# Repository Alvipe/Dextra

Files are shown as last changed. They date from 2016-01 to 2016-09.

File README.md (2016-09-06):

# Dextra
Dextra is a printable robotic hand with the size of a human hand. This project was initially started to build a replicable and low cost alternative to current robotic hand prostheses. However, I think this device has more potential uses, for example in robotics research (humanoid robotics, mobile platforms with manipulation capabilities) or in education, fields that could benefit from the existence of a cheap and easy to repair robotic hand, a robotic device that is replicable and hackable, and simple but functional.

<p align="center">
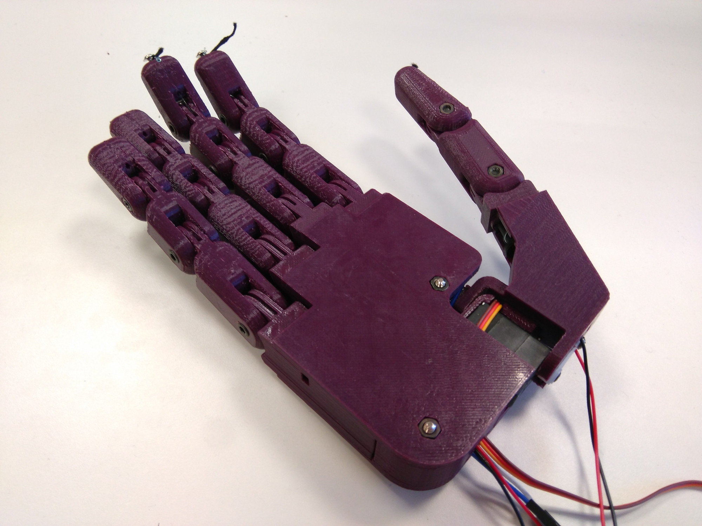
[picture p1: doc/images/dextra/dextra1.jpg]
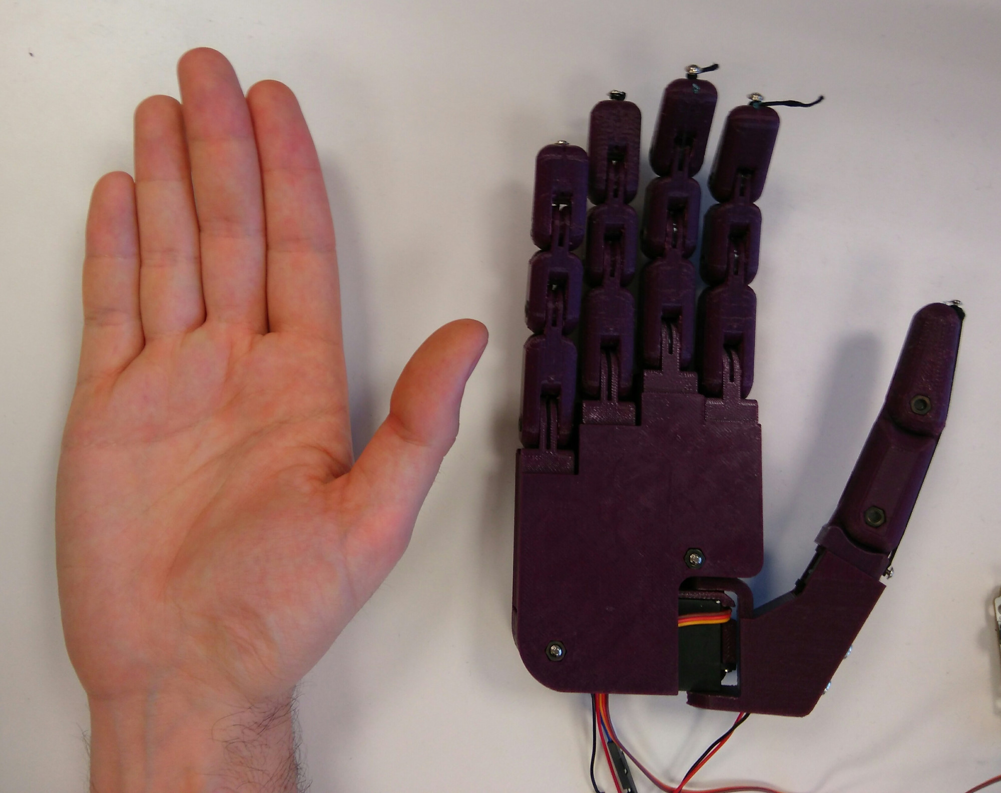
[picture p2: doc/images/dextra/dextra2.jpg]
    
</p>

The key design points of Dextra are: adaptive grip, compact size, mechanical simplicity and ease of replication. The mechanical design of Dextra revolves around the finger module the finger module, a modular part that comprises a compact linear actuator based on the Pololu 1000:1 Micro Metal Gearmotor HP, position feedback provided by a magnetic encoder, and the mechanical printable finger. This module is used in the four fingers of the hand, and the thumb is a variation of the same design. This makes assembly and repair simpler. Modular design also may favour the possibility of modifying the original design.

<p align="center">
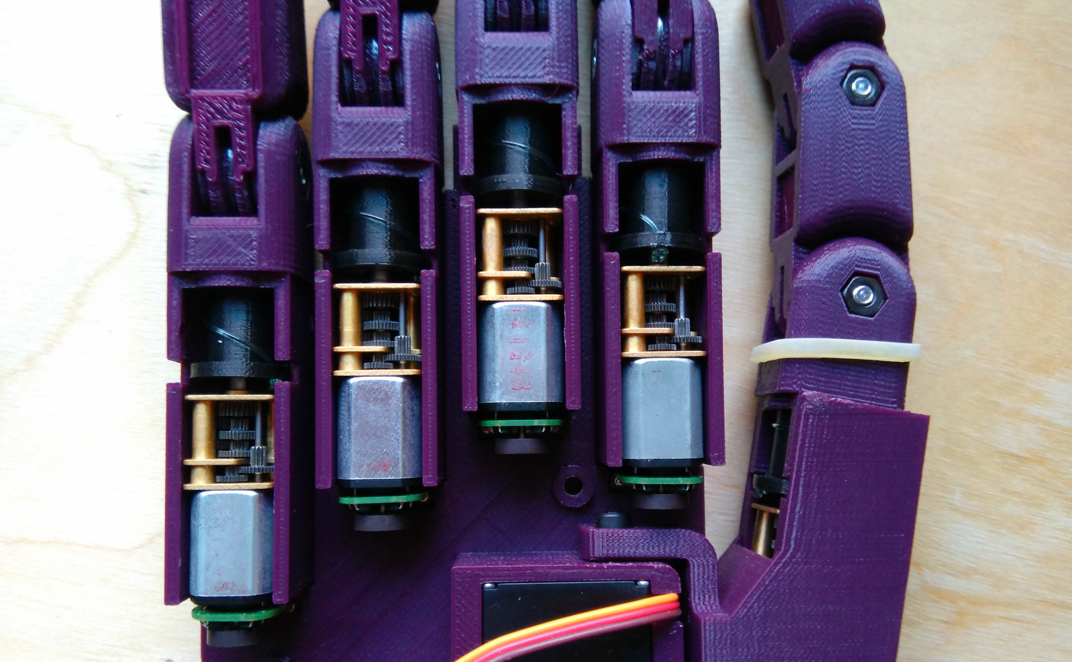
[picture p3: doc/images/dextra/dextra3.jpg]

</p>

The motion of the fingers of Dextra is controlled by a position control loop. Since the finger is underactuated, the angular position of each phalanx cannot be controlled independently. Instead, the total angular position of the finger, that is, the sum of the three joint angles, is controlled. Each finger is controlled by a PID loop that takes a position setpoint as the input and uses the feedback position measured by a magnetic quadrature encoder to adjust the real position of the DC motor driving the finger.

Dextra can be controlled either by sending commands from a computer with a GUI, or by using EMG signals, as would be done if the hand is used as a prosthesis. To implement the second type of control, an EMG interface called [Mumai](https://github.com/Alvipe/Mumai) is being used. Currently, a myoelectric threshold controller is implemented: the raw EMG signal provided by the EMG interface is rectified and smoothed by software and when this processed signal exceeds a certain value, the hand closes.

There is more information about Dextra on its [hackaday.io project page](https://hackaday.io/project/9890-dextra).

# Assembly instructions
The assembly instructions can be found [here](https://github.com/Alvipe/Dextra/tree/master/doc/dextra_assembly_instructions.pdf).

# Project index
* [Control](https://github.com/Alvipe/Dextra/tree/master/Control) - Code for different control methods (EMG, GUI)
* [Firmware](https://github.com/Alvipe/Dextra/tree/master/Firmware) - Main program and libraries that make Dextra move
* [Parts](https://github.com/Alvipe/Dextra/tree/master/Parts) - STL files of the printable parts of Dextra and its corresponding FreeCAD source files
* [doc](https://github.com/Alvipe/Dextra/tree/master/doc) - Documentation files

# License
<a rel="license1" href="https://www.gnu.org/licenses/gpl-3.0.html">GNU License</a>  

Code is licensed under the [GPL v3 License](https://www.gnu.org/licenses/gpl-3.0.html). The rest of the work is licensed under the [Creative Commons Attribution-ShareAlike 4.0 International License](http://creativecommons.org/licenses/by-sa/4.0/).

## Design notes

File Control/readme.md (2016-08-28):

The Dextra Control GUI is designed using [Kivy](https://kivy.org/#home). Besides having Python installed, this library and its dependencies are required to run the application. The application uses both the *.py* and the *.kv* files, and they need to be in the same folder.

To run the control GUI, connect the microcontroller running the Dextra firmware to a USB port of the computer, and run:

```bash
~/Dextra$ cd Control
~/Dextra/Control$ python DextraControl.py
```

First, the device to which we want to communicate (the microcontroller running the Dextra firmware) has to be selected from a dropdown list. Once the desired device is selected (in this case the one connected to COM4; in this example the app is running on a Windows PC), we click on the connect button. If there is no device connected to the PC, or no device is selected from the dropdown list, an error message is displayed.

<p align="center">
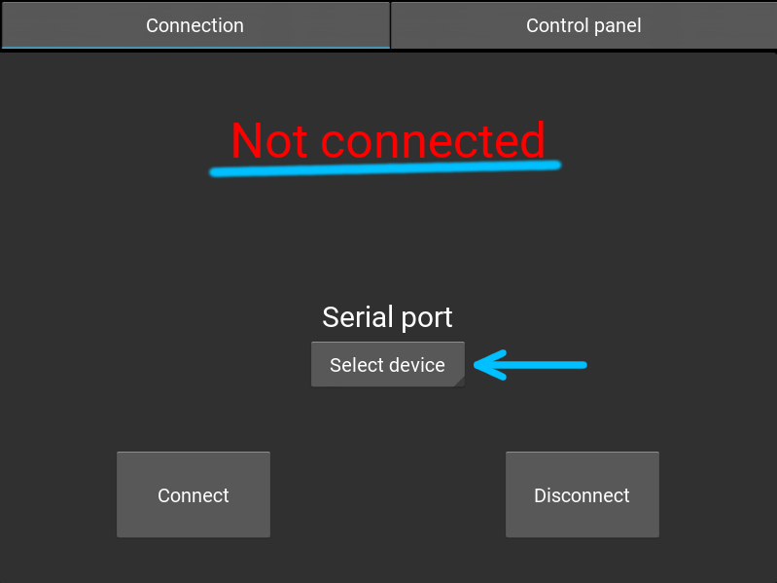
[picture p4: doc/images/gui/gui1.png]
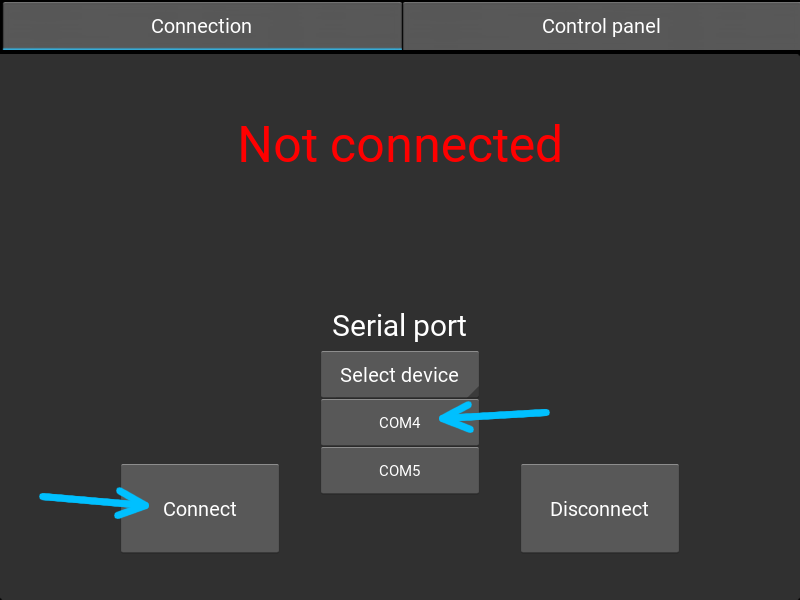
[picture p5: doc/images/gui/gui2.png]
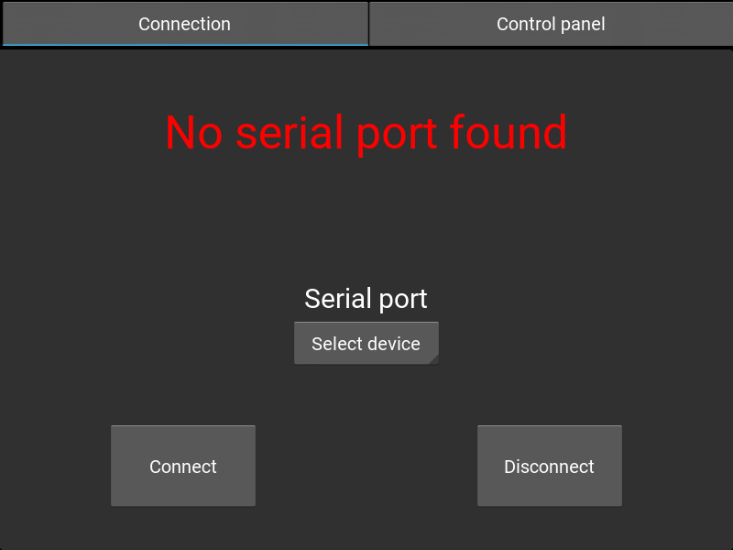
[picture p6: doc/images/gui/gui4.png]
        
</p>

If the connection is successful, we can select the *Control panel* tab. In this tab, we can control the position of each finger and the abduction angle of the thumb. The position values can be inputted by using the text boxes or by moving the sliders.

<p align="center">
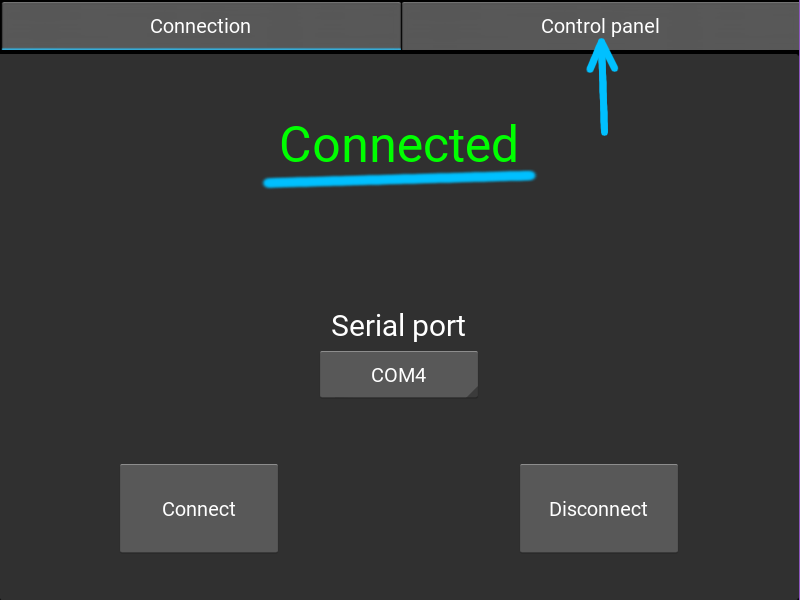
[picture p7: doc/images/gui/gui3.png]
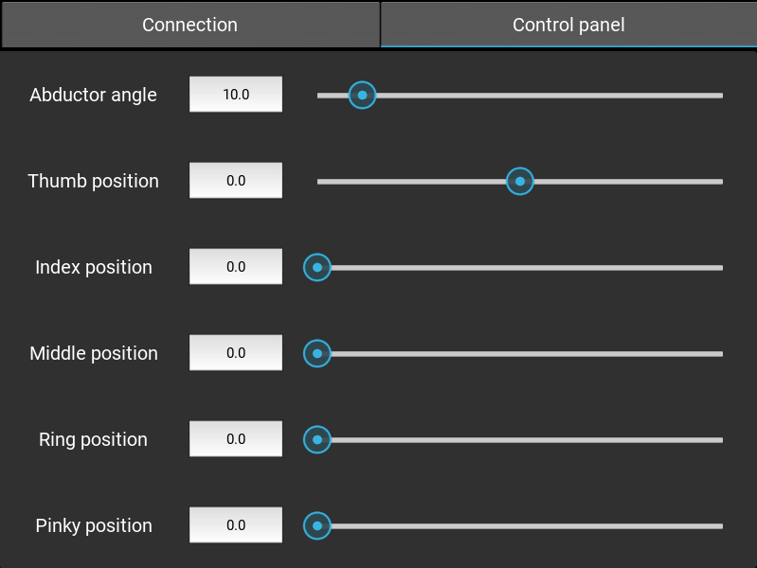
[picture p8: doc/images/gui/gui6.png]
    
</p>

To stop communicating with the microcontroller, we select the *Connection* tab and click the disconnect button.

<p align="center">
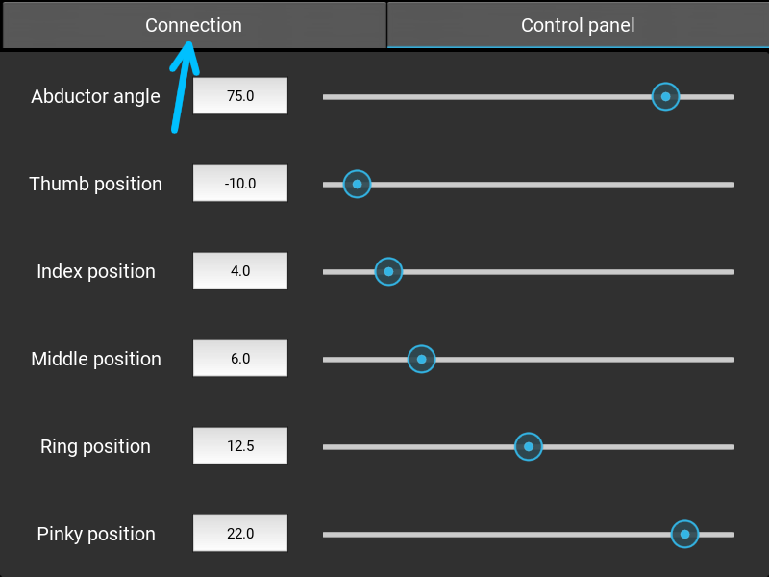
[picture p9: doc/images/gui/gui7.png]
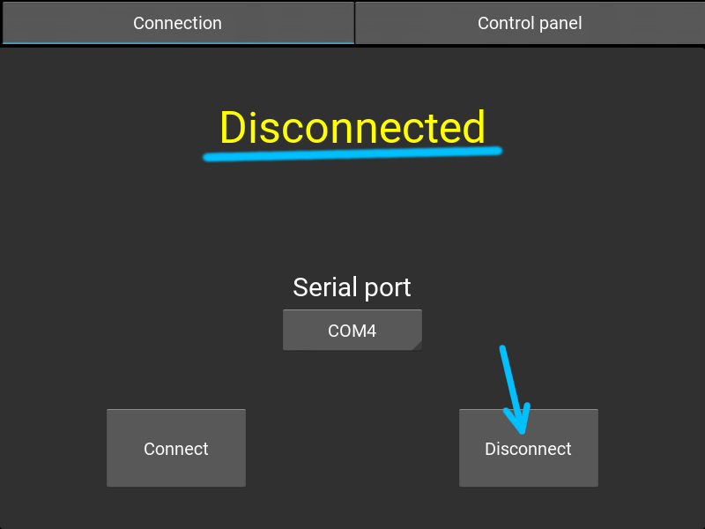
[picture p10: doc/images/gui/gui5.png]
    
</p>

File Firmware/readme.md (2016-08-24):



To upload the firmware to one of the supported boards, use [platformio](http://platformio.org/).

For Teensy 3.1 (Arduino-compatible board):
```bash
~/Dextra$ cd Firmware/Teensy31
~/Dextra/Firmware/Teensy31$ platformio run --target upload
```

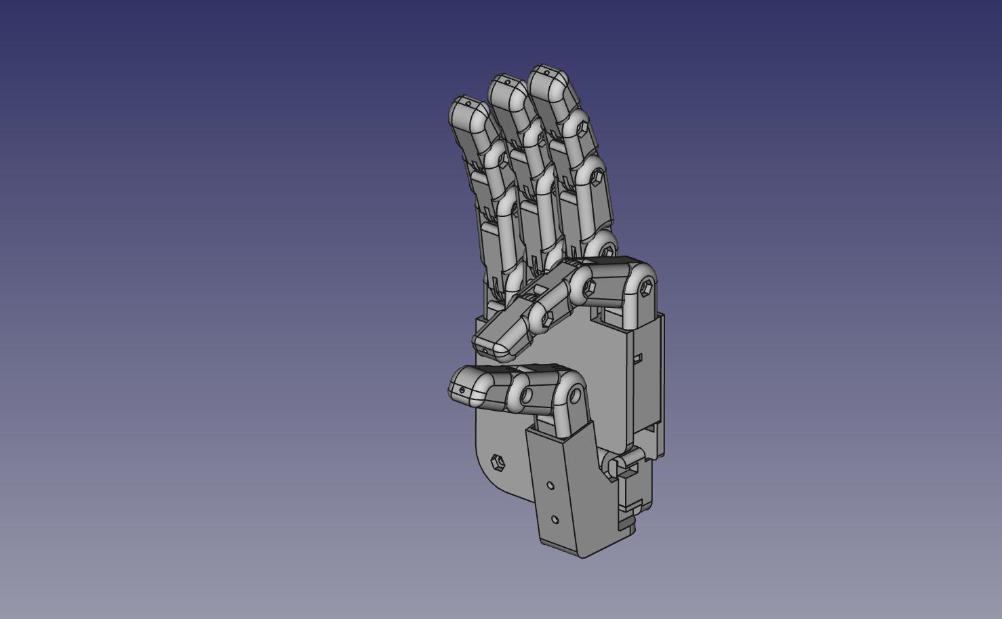
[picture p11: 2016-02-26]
doc/images/dextra/palmar_pinch_grasp.jpg

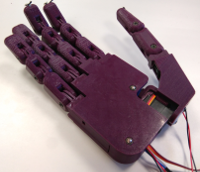
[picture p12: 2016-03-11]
doc/images/dextra.png

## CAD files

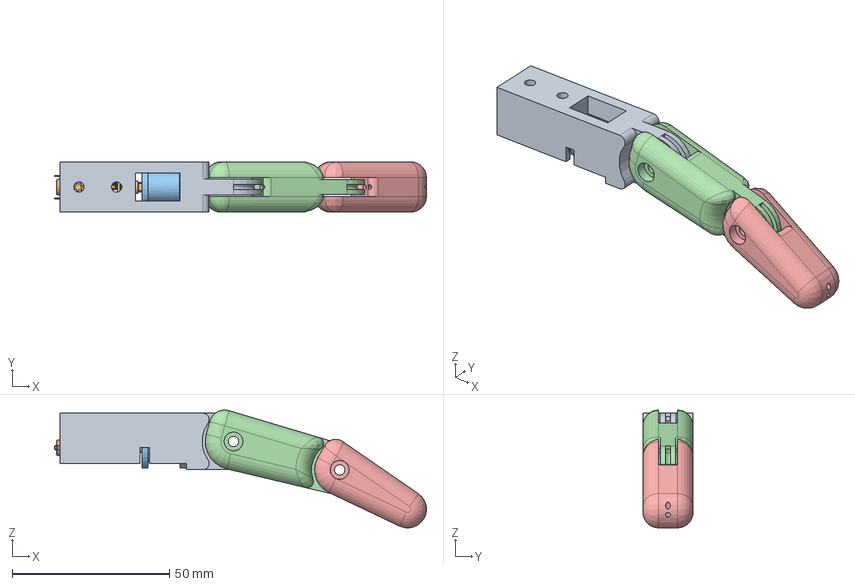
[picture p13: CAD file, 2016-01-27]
Hand/Parts/FreeCAD files/Assembly/thumb_module.fcstd
118.5 x 16.0 x 37.6 mm
motor_holder_01
pololu_motor_01
winder_01
proximal_01
distal_thumb_01

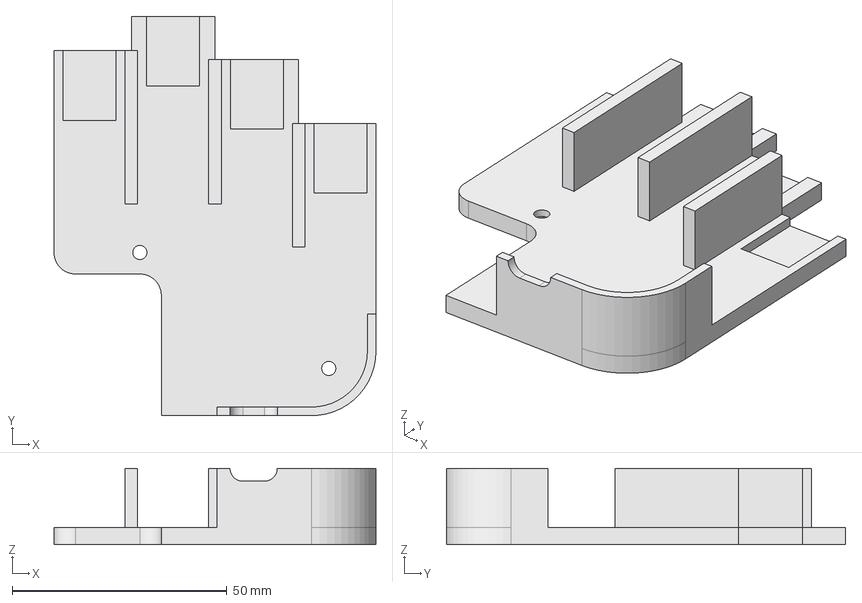
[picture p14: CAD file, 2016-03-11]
Parts/FreeCAD files/palm.fcstd
75.0 x 93.0 x 17.8 mm

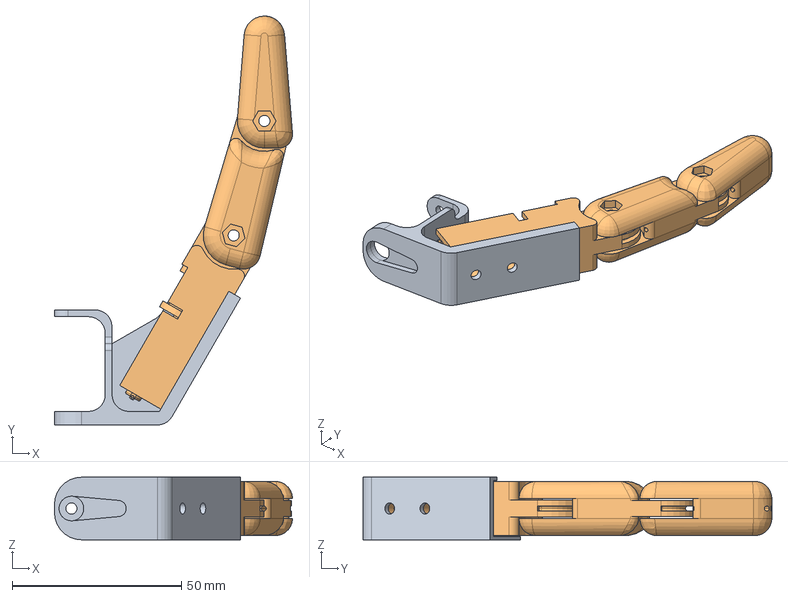
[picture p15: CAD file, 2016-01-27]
Hand/Parts/FreeCAD files/Assembly/thumb.fcstd
70.3 x 120.8 x 18.5 mm
abductor_01
thumb_module_01

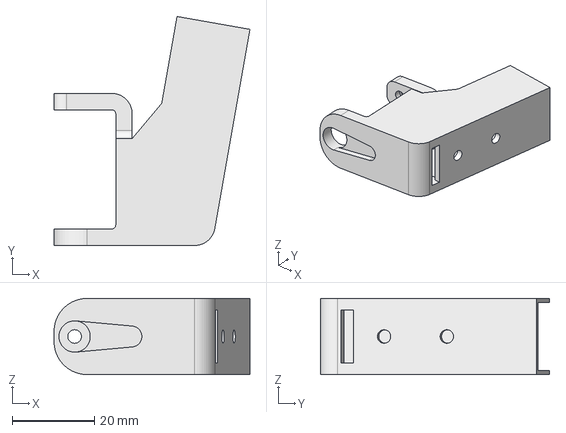
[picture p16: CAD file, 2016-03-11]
Parts/FreeCAD files/abductor.fcstd
47.6 x 55.7 x 18.5 mm

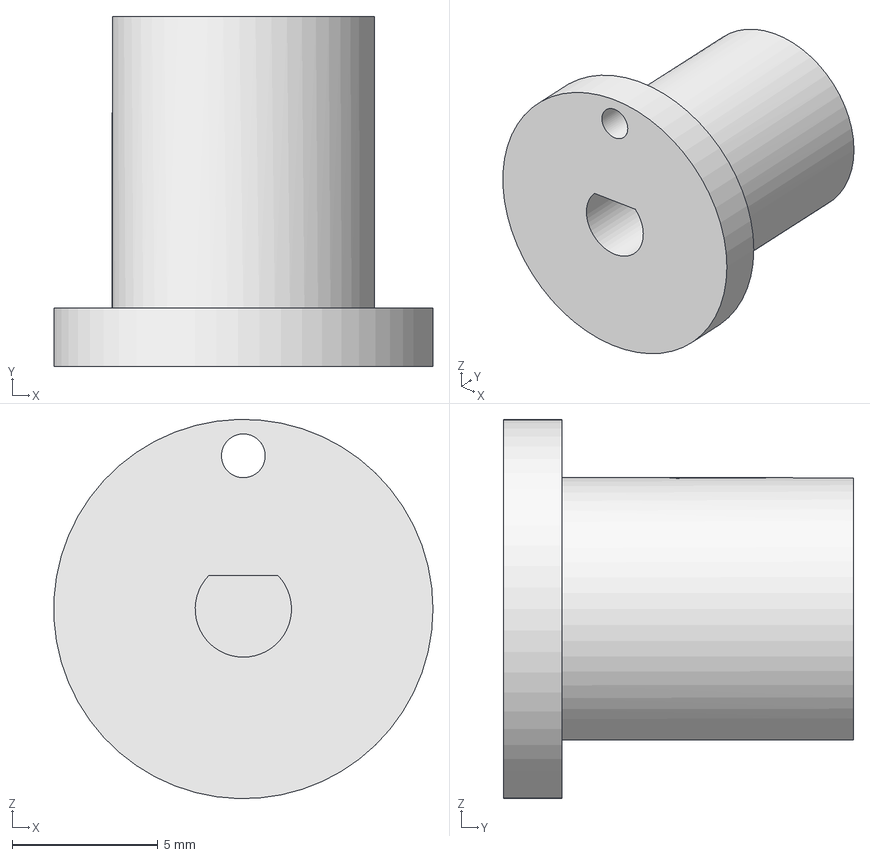
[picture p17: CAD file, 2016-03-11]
Parts/FreeCAD files/spool.fcstd
13.0 x 12.0 x 13.0 mm

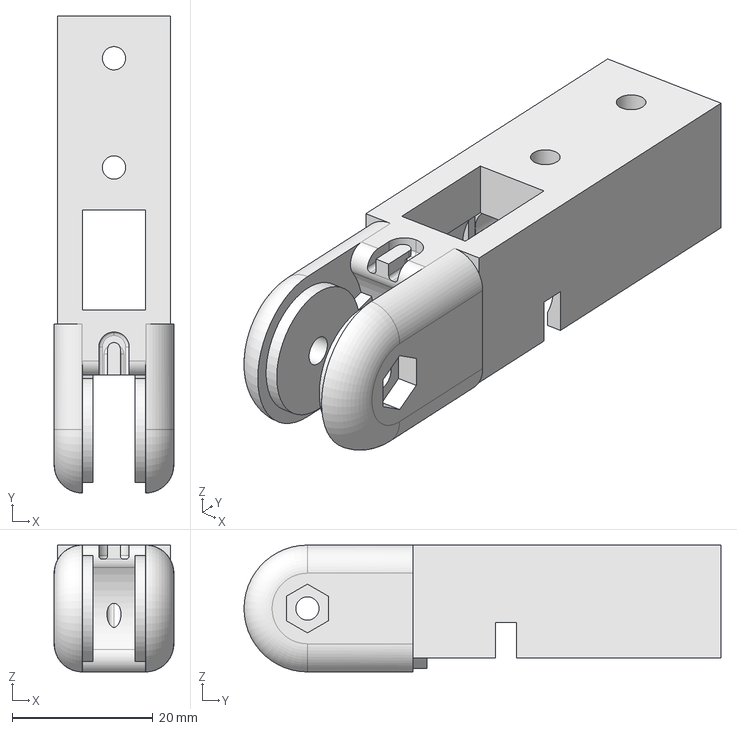
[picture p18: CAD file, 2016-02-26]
Parts/FreeCAD files/motor_holder_thumb.fcstd
17.0 x 67.7 x 18.0 mm

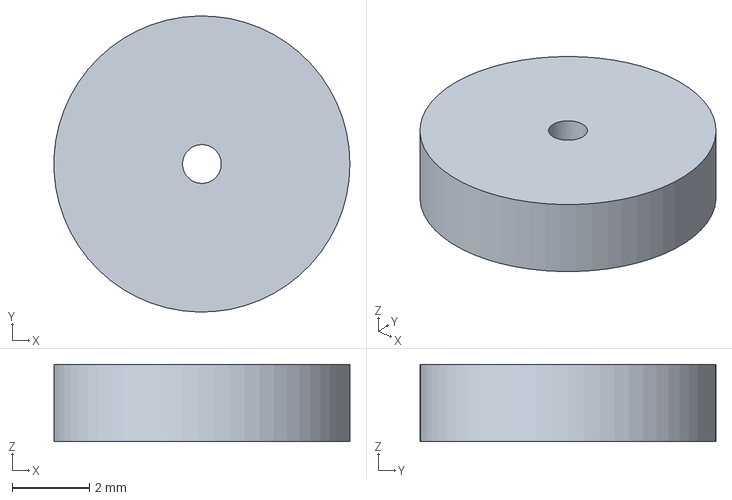
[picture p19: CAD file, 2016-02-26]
Parts/FreeCAD files/encoder_disc.fcstd
7.64 x 7.65 x 2.00 mm

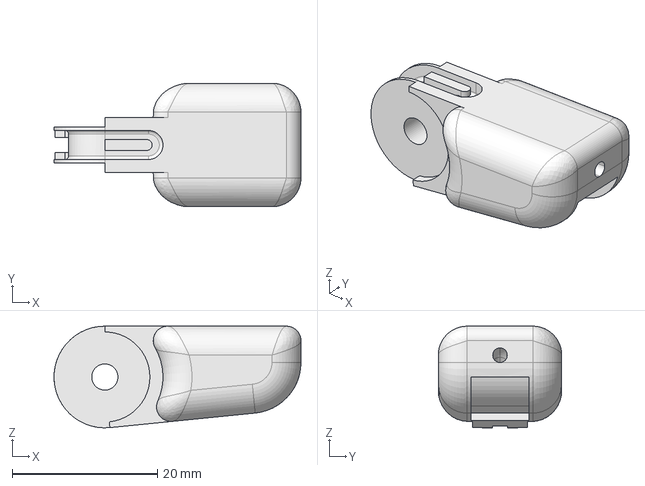
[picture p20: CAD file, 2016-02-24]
Parts/FreeCAD files/distal.fcstd
34.0 x 17.0 x 14.0 mm

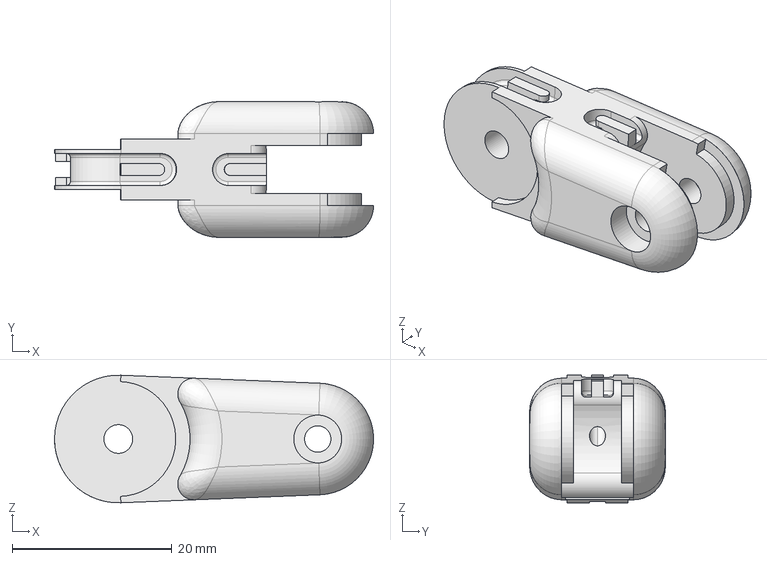
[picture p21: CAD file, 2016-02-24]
Parts/FreeCAD files/middle.fcstd
40.0 x 17.0 x 16.0 mm

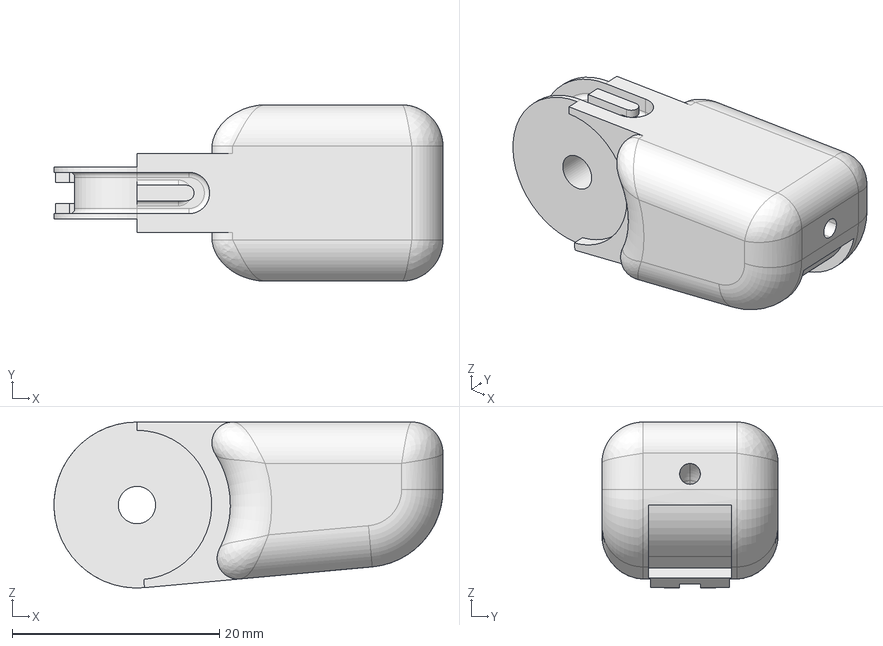
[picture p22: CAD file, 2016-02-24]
Parts/FreeCAD files/distal_thumb.fcstd
37.5 x 17.0 x 16.0 mm

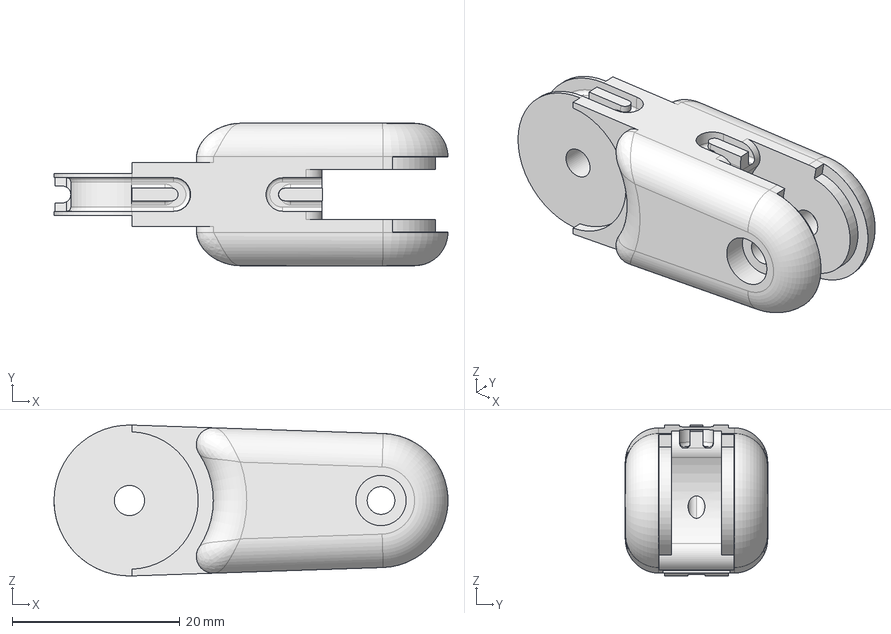
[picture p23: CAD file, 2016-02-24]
Parts/FreeCAD files/proximal_thumb.fcstd
47.0 x 17.0 x 18.0 mm

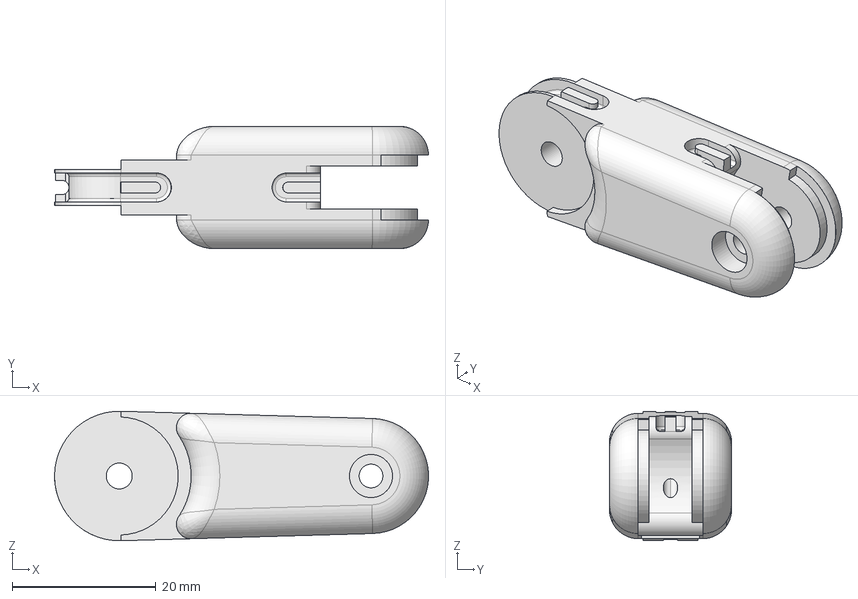
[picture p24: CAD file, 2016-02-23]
Parts/FreeCAD files/proximal.fcstd
52.0 x 17.0 x 18.0 mm

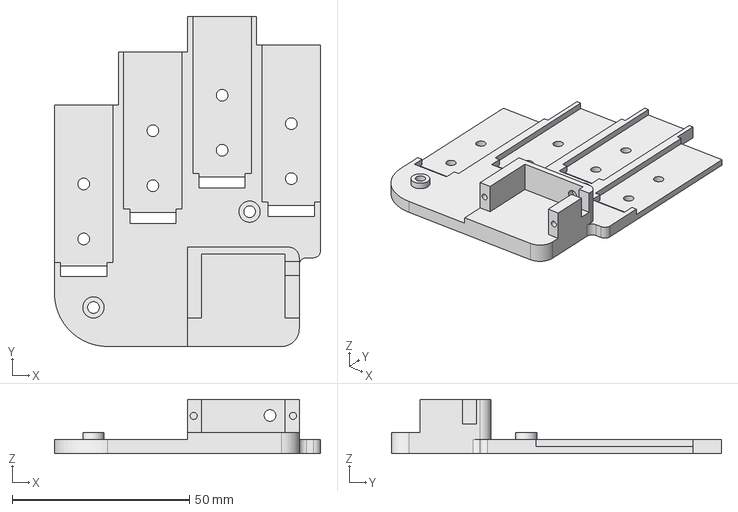
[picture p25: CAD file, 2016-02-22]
Parts/FreeCAD files/dorsal.fcstd
75.0 x 93.0 x 15.3 mm

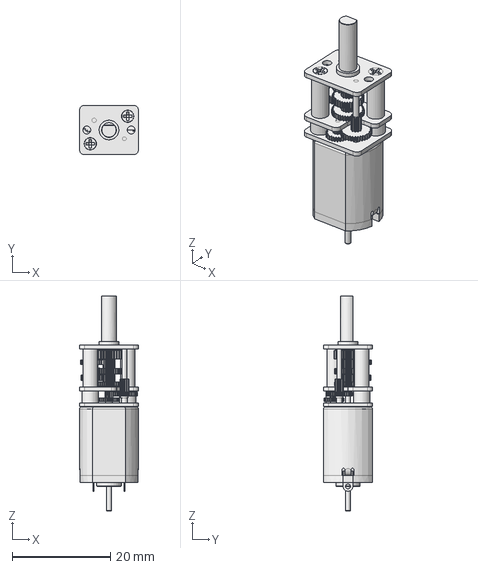
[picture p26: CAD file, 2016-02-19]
Parts/FreeCAD files/pololu_motor_10001.fcstd
12.0 x 10.0 x 43.7 mm

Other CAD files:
Parts/FreeCAD files/motor_holder.fcstd
Parts/FreeCAD files/Turnigy TGY-EX5252.FCStd
Parts/FreeCAD files/servo_horn.fcstd
Parts/abductor.stl
Parts/distal.stl
Parts/distal_thumb.stl
Parts/dorsal.stl
Parts/middle.stl
Parts/motor_holder.stl
Parts/motor_holder_thumb.stl
Parts/palm.stl
Parts/proximal.stl
Parts/proximal_thumb.stl
Parts/spool.stl

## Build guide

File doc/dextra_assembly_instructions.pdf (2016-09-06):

# Dextra v1.0 assembly instructions

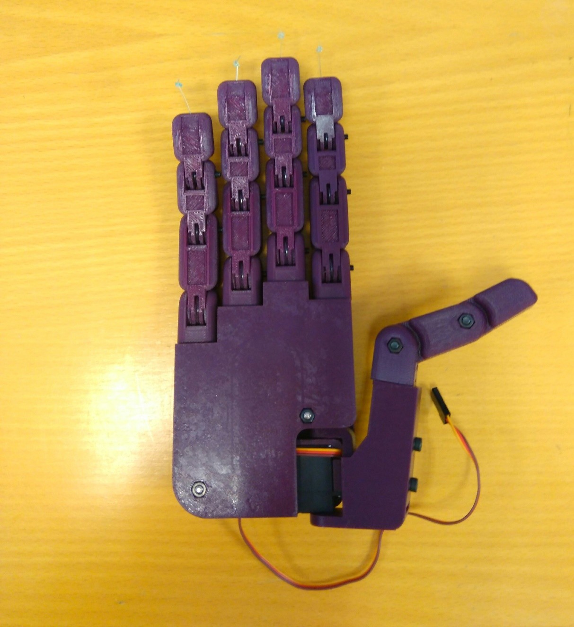
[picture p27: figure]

## Author: Álvaro Villoslada (Alvipe)

License: Creative Commons Attribution-ShareAlike 4.0 International License

This is a step-by-step visual guide to assemble a Dextra hand. You can find the design files, firmware, code to control the hand and more details about this project on its Github repository (https://github.com/Alvipe/Dextra) and on its hackaday.io project page (https://hackaday.io/project/9890-dextra).

Before starting the assembly, all the mechanical parts of Dextra should be printed. The .stl files are available on both links above and on Thingiverse (https://www.thingiverse.com/thing:1538508).

NOTICE: these instructions are to assemble a Dextra hand v1.0. Future versions of Dextra may have different features with respect to this version and assembly steps may be different to the ones explained in this document.

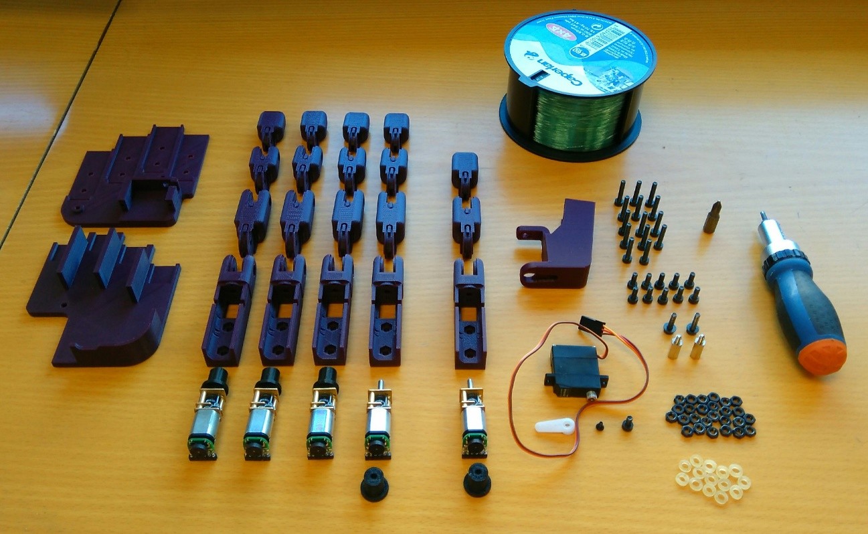
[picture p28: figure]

These are all the components needed to assemble a Dextra hand: 3D printed parts:
- 4x finger module:
- 4x motor_holder.
- 4x proximal.
- 4x middle.
- 4x distal.
- 1x thumb module:
- 1x motor_holder_thumb.
- 1x proximal_thumb.
- 1x distal_thumb.
- 5x spool.
- 1x abductor.
- 1x dorsal.
- 1x palm.
Other components:
- 5x Pololu Micro Metal Gearmotor 1000:1 HP with extended motor shaft.
- 5x Pololu magnetic encoder for Micro Metal Germotors.
- 5x right angle female connector (2mm pitch).
- 1x Turnigy TGY-EX5252MG Twin BB Digital Micro Servo.
- 1x fishing line spool.
- 14x small rubber bands (orthodontic elastic bands).
- 14x M3x14 bolt.
- 10x M3x8 bolt.
- 2x M3x12 bolt.
- 1x M3x6 bolt.
- 2x M3x12 spacer.
- 26x M3 nut.

Tools:
- 2.5 mm Allen key (for M3 bolts).
- Phillips screwdriver (for servomotor bolts).
- Needle file or sandpaper (to rework the 3D printed parts if needed).
- Scissors (to cut the fishing line).
- Soldering iron and solder.

Step 1 (Actuator assembly):
The first step is assembling the micro actuator that pulls and releases the tendons.
To assemble one micro actuator we need:
- 1x Pololu Micro Metal Gearmotor 1000:1 HP with extended motor shaft.
- 1x Pololu magnetic encoder for Micro Metal Germotors.
- 1x right angle female connector (2mm pitch).
- 1x spool (printed part).

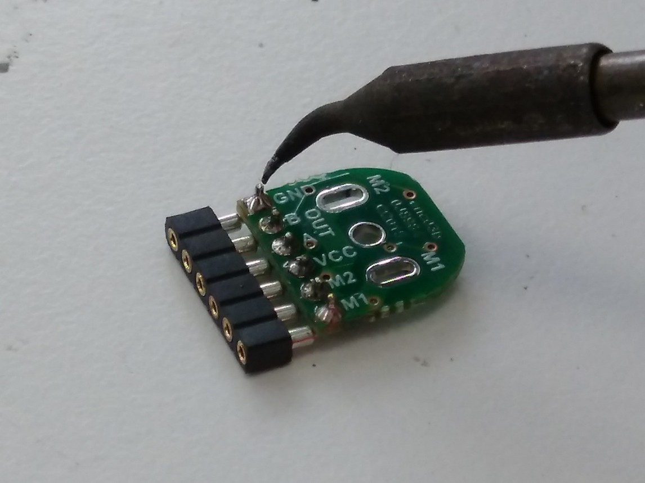
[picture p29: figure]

First, we have to integrate the magnetic encoder into the micro motor. Solder the 2 mm pitch right angle connector to the encoder PCB. The pins have to be soldered on the side of the PCB that has text labels and no components, as the image above shows.

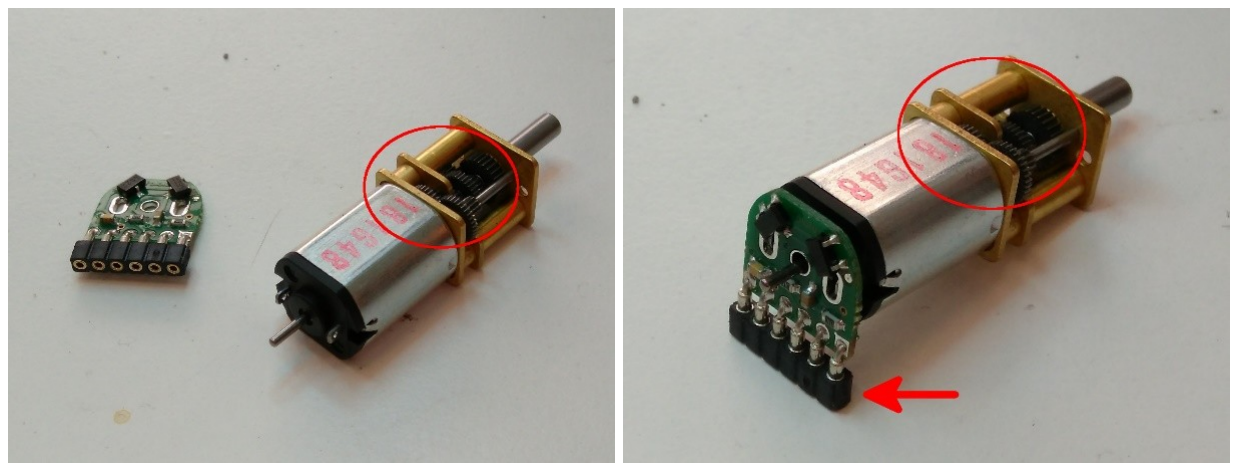
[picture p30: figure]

The encoder has to be installed as in the pictures above. Put the encoder PCB on the back of the micro motor with the side that has no components facing the back side of the motor, and with the female pins facing the side of the motor opposite to the one that has a small gap in the gearbox.

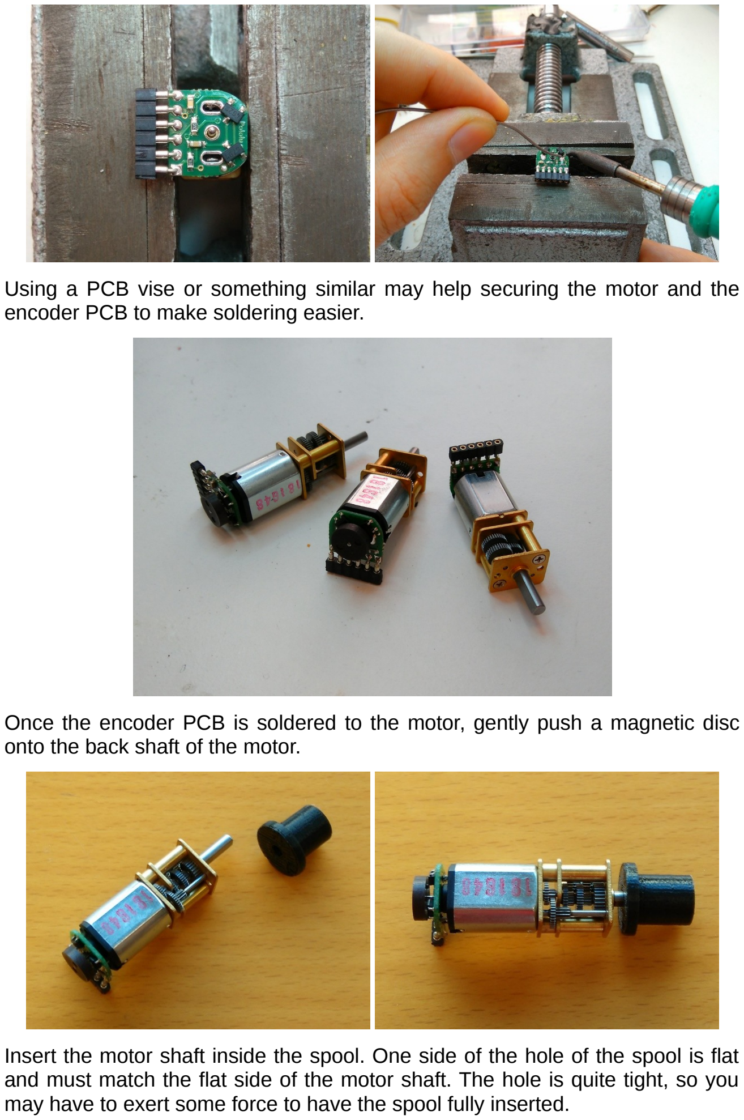
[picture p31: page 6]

Using a PCB vise or something similar may help securing the motor and the encoder PCB to make soldering easier.

Once the encoder PCB is soldered to the motor, gently push a magnetic disc onto the back shaft of the motor.

Insert the motor shaft inside the spool. One side of the hole of the spool is flat and must match the flat side of the motor shaft. The hole is quite tight, so you may have to exert some force to have the spool fully inserted.

Step 2 (finger module assembly):

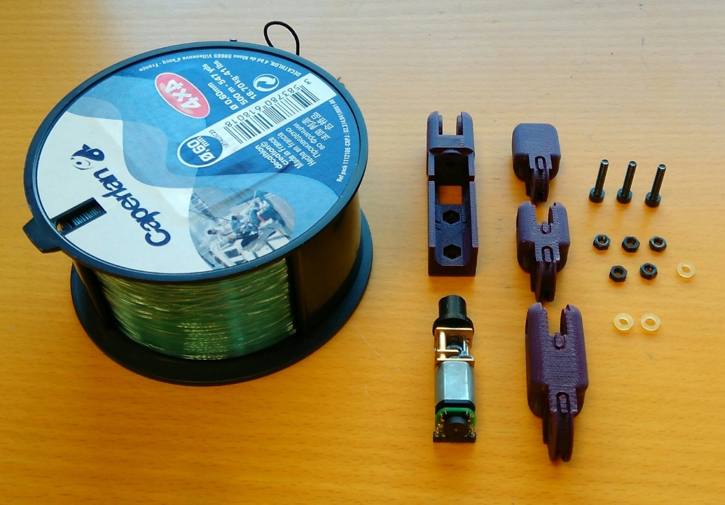
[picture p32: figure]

After we have all the micro actuators assembled, we are going to assemble the finger modules and the thumb module. The finger module is the same for the four fingers, and the thumb module is practically the same (it has two phalanxes and more range of motion on the proximal joint), so these steps are the same for all the fingers.
To assemble one finger module we need:
- 1x assembled actuator.
- 1x motor_holder (printed part).
- 1x proximal (printed part).
- 1x middle (printed part).
- 1x distal (printed part).
- 3x M3x14 bolt.
- 5x M3 nut.
- 3x small rubber band.
- Fishing line.

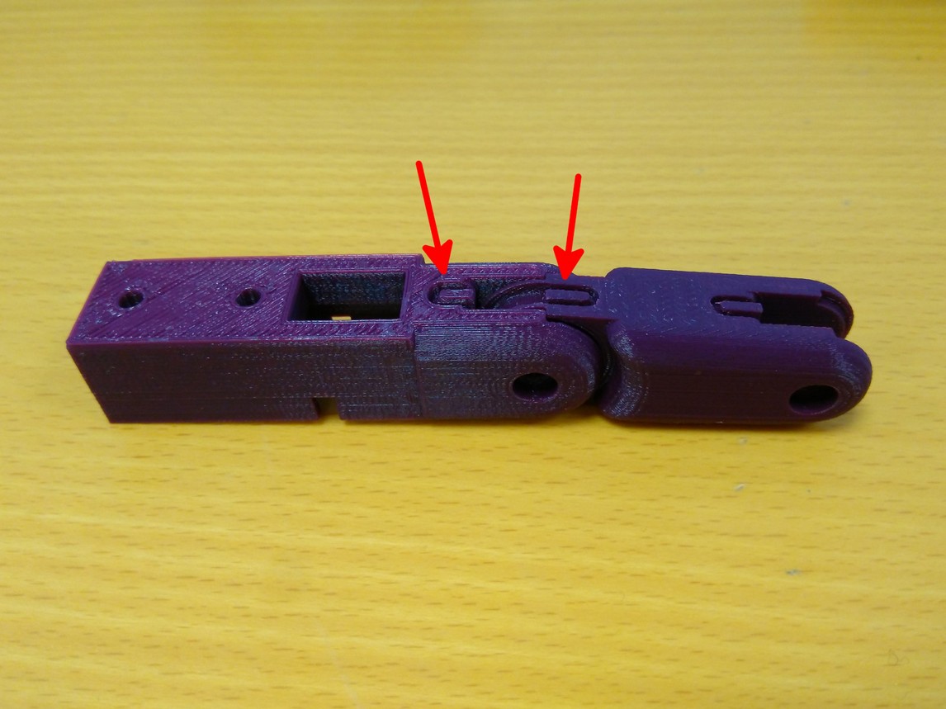
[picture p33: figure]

We are going to assemble the first joint of the finger module, the proximal joint. Insert the “male” joint of the proximal part into the “female” joint of motor holder part as the image shows, making the sides with the notch match. Make sure that the proximal part is able to freely rotate without friction. Sand the inner faces of the “female” joint of the motor holder part if necessary.

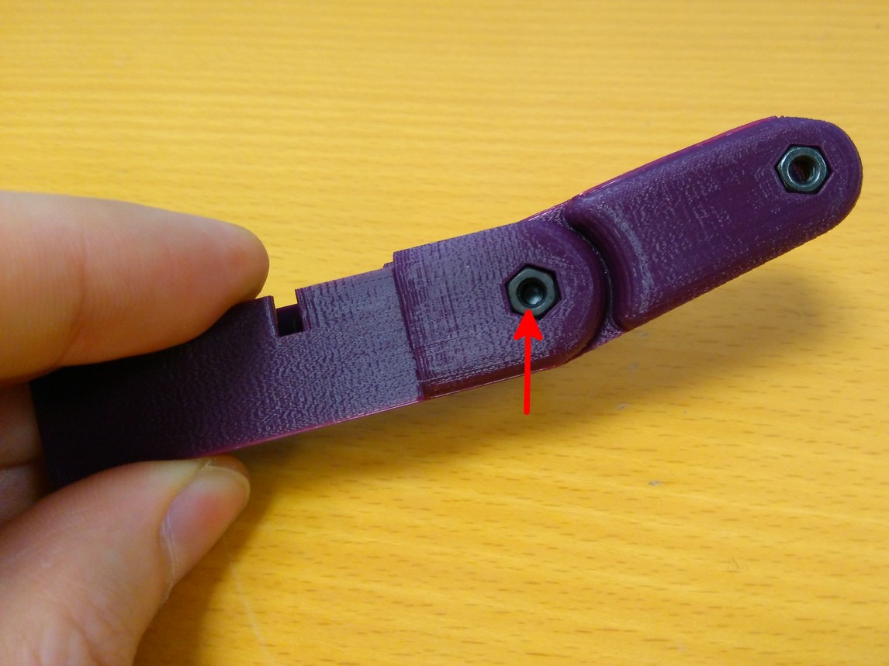
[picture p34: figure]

Insert a M3 nut inside its corresponding hexagonal hole. Screw a M3x14 bolt in the M3 nut to join the proximal phalanx to the motor holder forming an articulated joint.

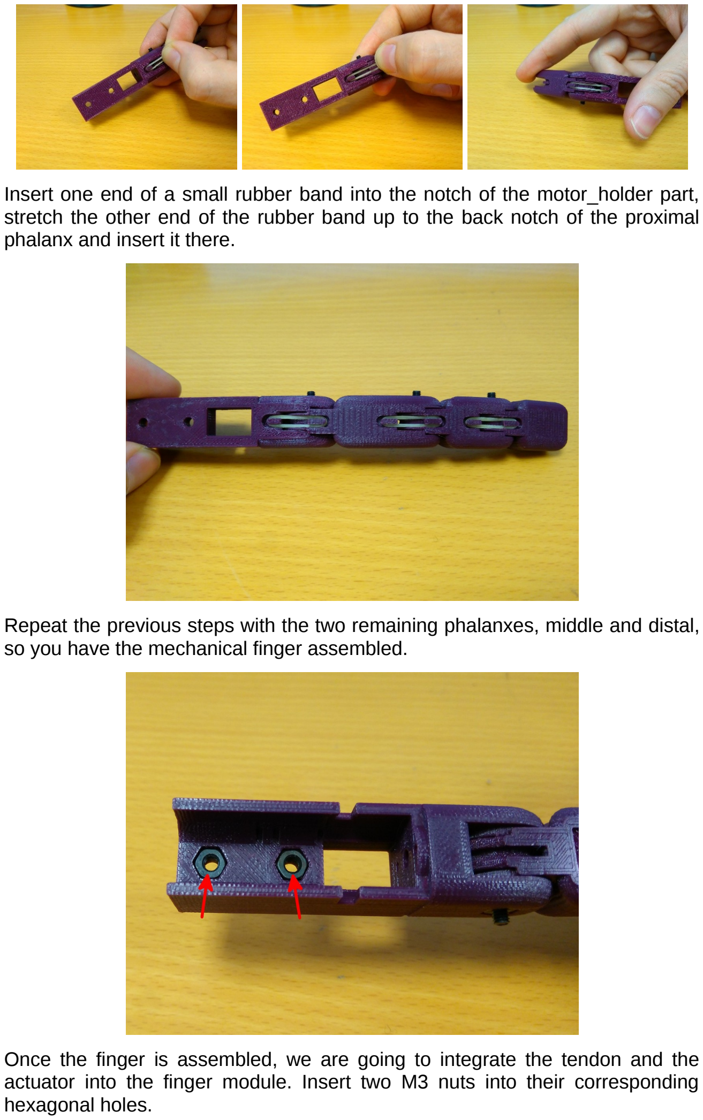
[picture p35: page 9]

Insert one end of a small rubber band into the notch of the motor_holder part, stretch the other end of the rubber band up to the back notch of the proximal phalanx and insert it there.

Repeat the previous steps with the two remaining phalanxes, middle and distal, so you have the mechanical finger assembled.

Once the finger is assembled, we are going to integrate the tendon and the actuator into the finger module. Insert two M3 nuts into their corresponding hexagonal holes.

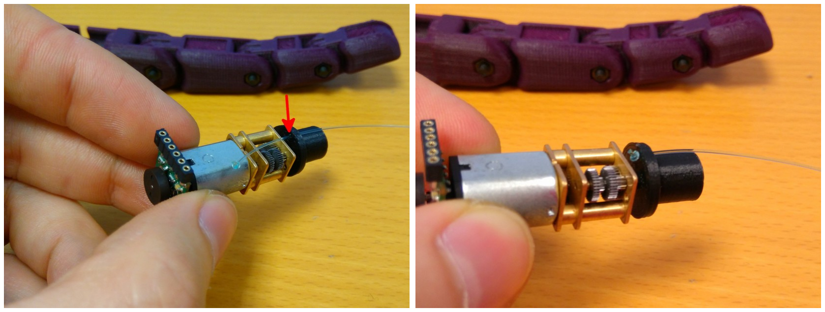
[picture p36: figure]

Cut a string of fishing line of approximately 15 cm long and make a knot in one of its ends. You can put a drop of glue on the knot to make sure it does not loosen. Pass the other end through the small hole in the spool (if the hole is too small, use a sewing pin to widen it). Pull the tendon until the knot touches the spool.

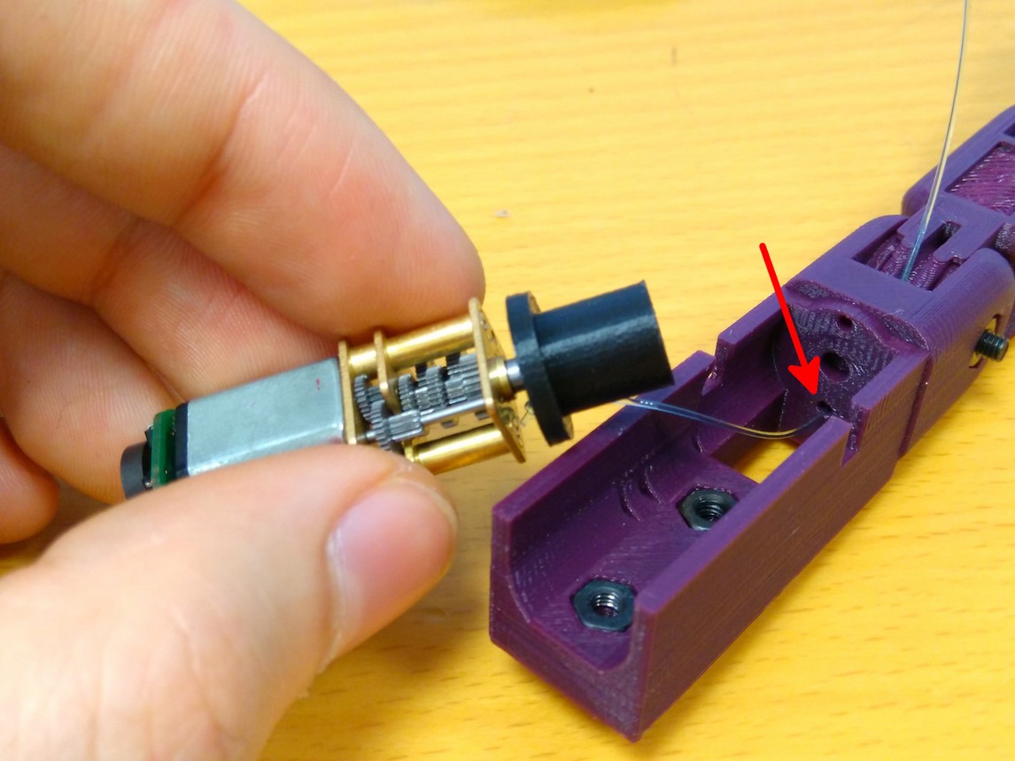
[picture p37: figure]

Pass the free end of the tendon through the small hole on the lower side of the motor holder part (see the image above).

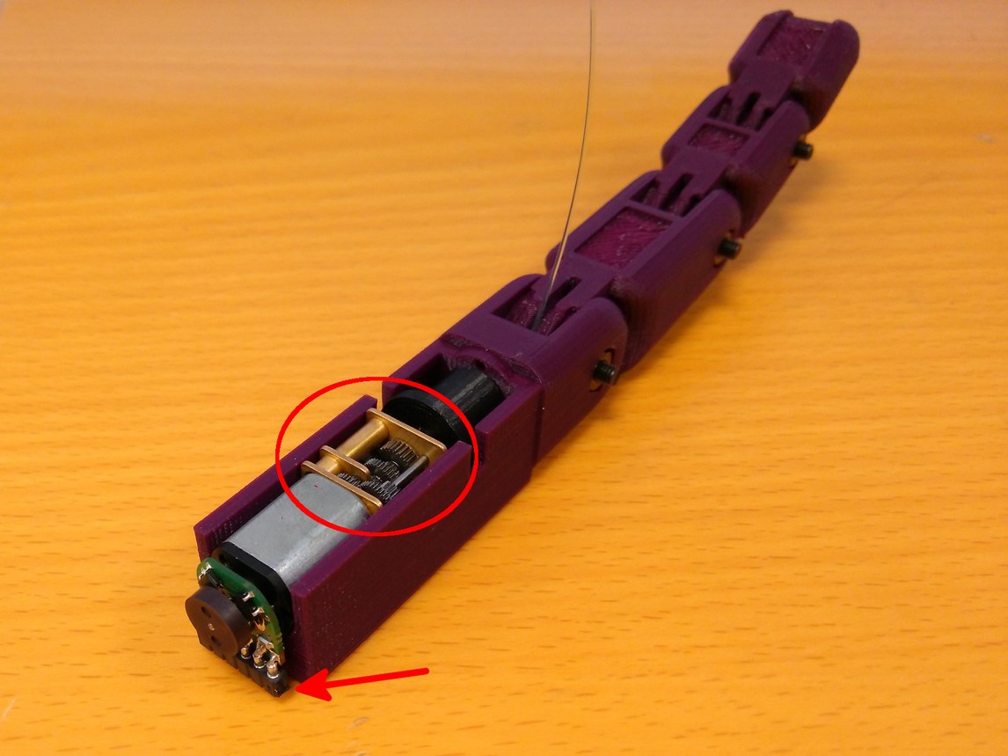
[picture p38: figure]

Pull the tendon and insert the actuator into its housing. The actuator has to be installed as in the image above, with the side of the gearbox with a small gap facing upwards and the female pins of the encoder facing downwards.

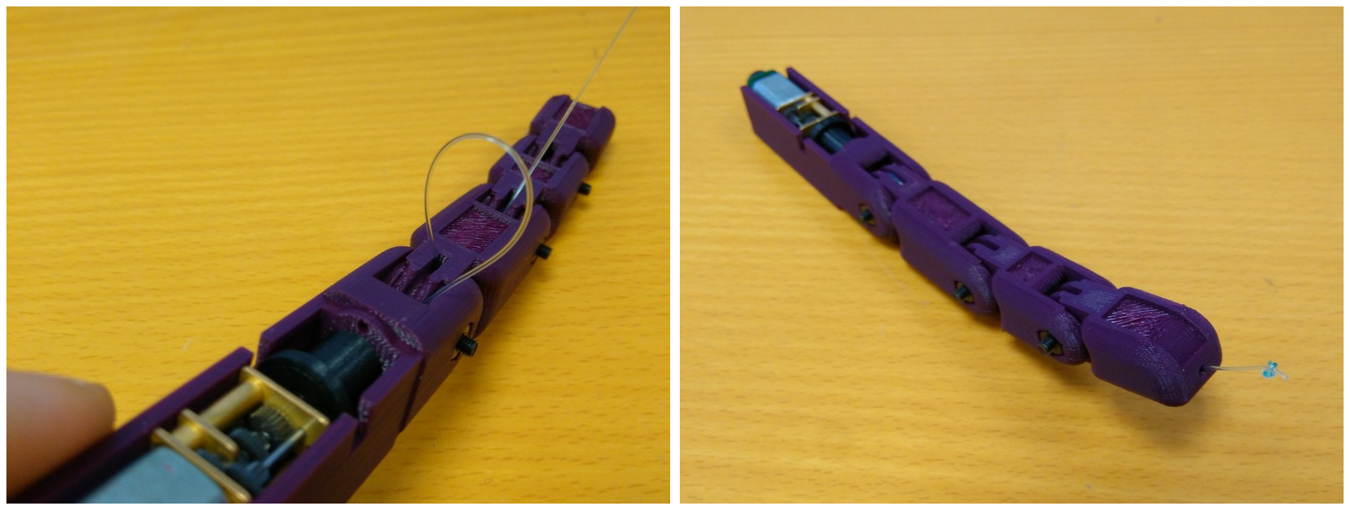
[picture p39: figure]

Pass the free end of the tendon through the tendon channels of the three phalanxes until it comes out through the hole on the tip of the distal phalanx. Make a double knot close to the tip of the finger and cut the remaining wire. Once again, you can put a drop of glue on the knot to make sure it does not loosen. Do not worry if the tendon protrudes slightly because, once the hand is assembled, the actuators can be slowly rotated until the tendon is taut.

Step 3 (dorsal assembly):

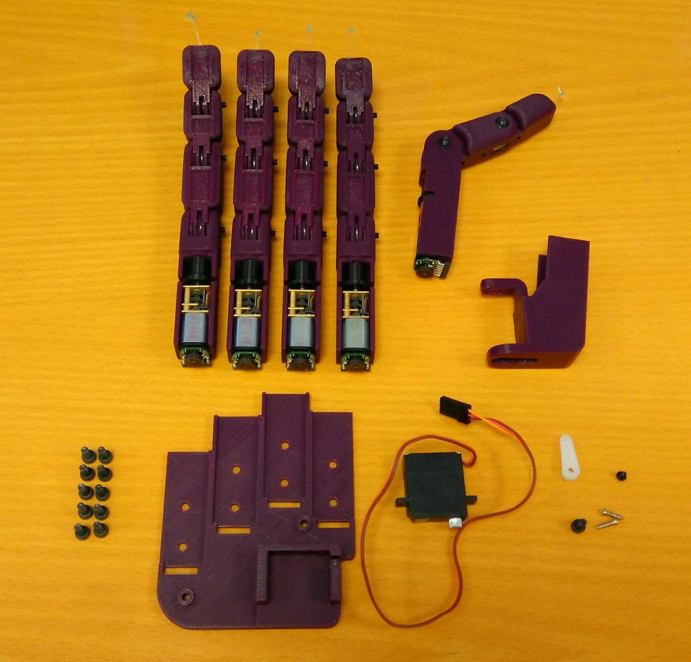
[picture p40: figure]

Once we have assembled the four finger modules and the thumb module, we are going to fix them to the structural piece of the hand, the dorsal part.
For this step we need:
- 4x assembled finger modules.
- 1x assembled thumb module.
- 1x Turnigy TGY-EX5252MG Twin BB Digital Micro Servo.
- 1x dorsal (printed part).
- 1x abductor (printed part).
- 10x M3x8 bolt.
- 1x M3x6 bolt.

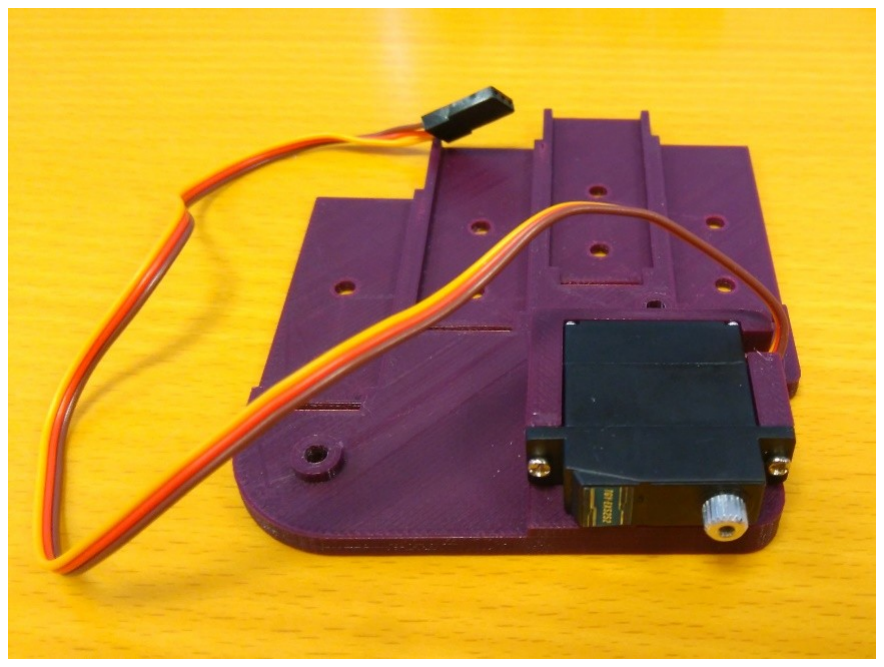
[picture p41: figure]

First, we have to assemble the abduction mechanism. Insert the servomotor into its housing as depicted in the image above, with the cable coming out through the small gap in the housing. Fix the servomotor to the dorsal part with the two little screws that come with the motor.

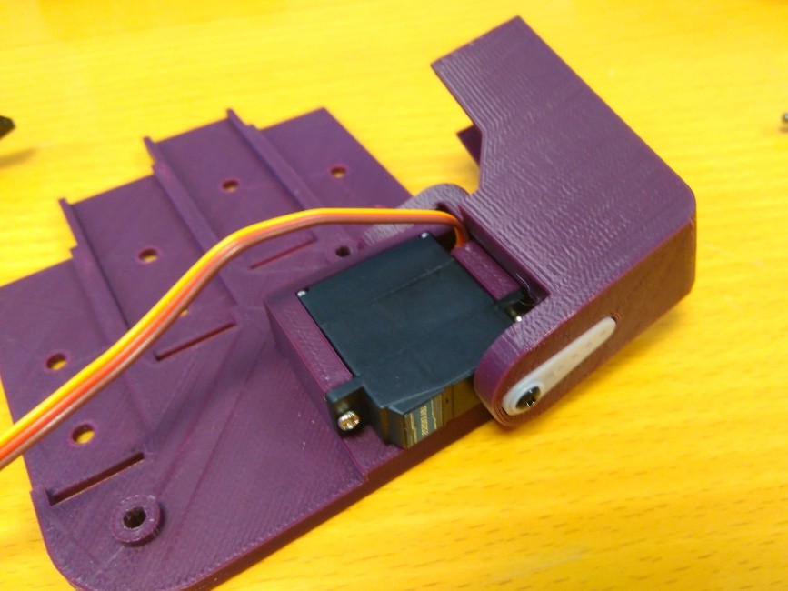
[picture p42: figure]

Insert the servo horn inside its hole on the abductor part and fix it with one or two little screws. Place the horn on the servomotor shaft and fix it with the small screw that comes with the motor for this purpose. Screw the M3x6 bolt through the small hinge of the abductor part to the servomotor housing of the dorsal part.

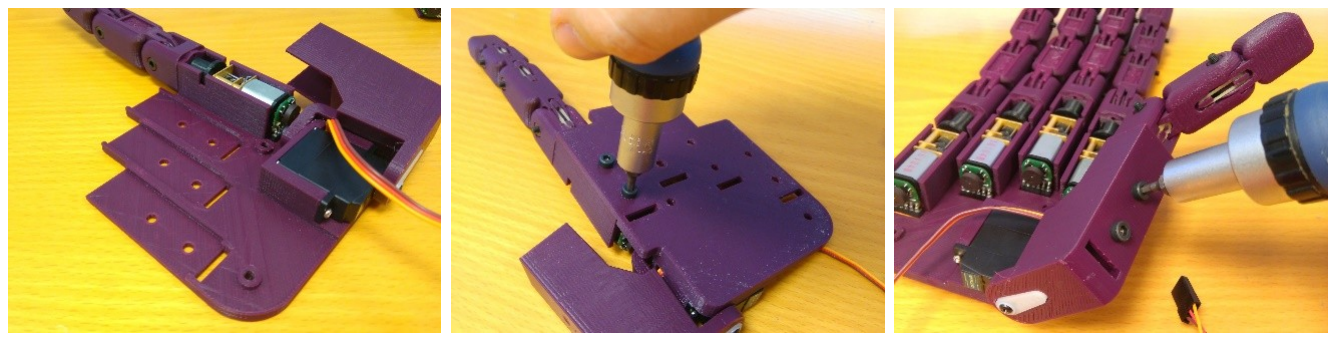
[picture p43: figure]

Put one finger module on its corresponding place and screw two M3x8 bolts to secure it in place. Repeat for the rest of the finger modules and for the thumb module.

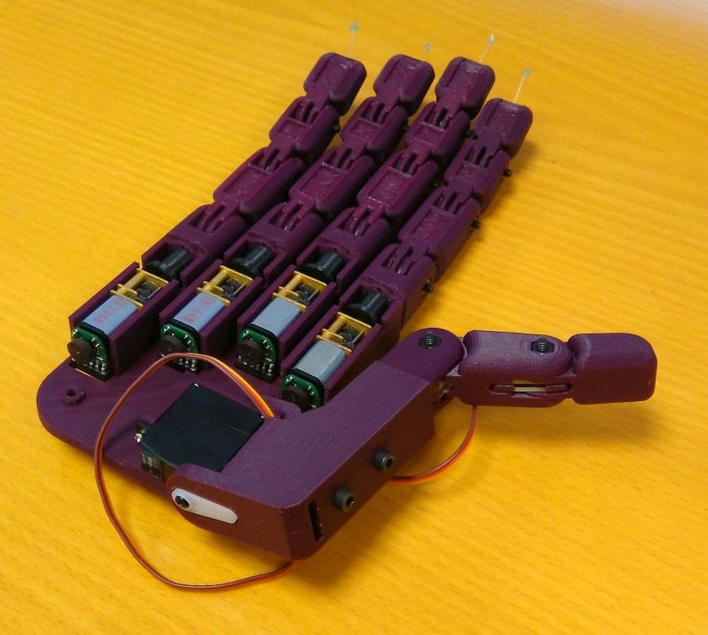
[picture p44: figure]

Step 4 (palm assembly):
The last step to have a fully assembled Dextra hand is placing the cover that protects the actuators, the palm part.
For this step we need:
- 1x palm (printed part).
- 2x M3x12 spacer.
- 2x M3x12 bolt.
- 2x M3 nut.

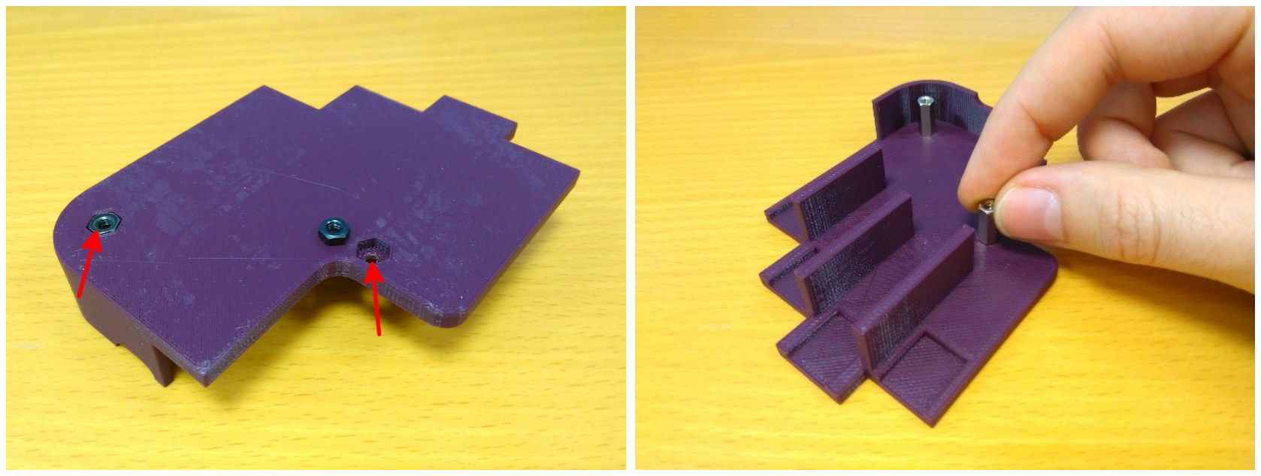
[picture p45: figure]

Insert two M3 nuts into their hexagonal holes. Screw the two M3x12 spacers to these nuts.

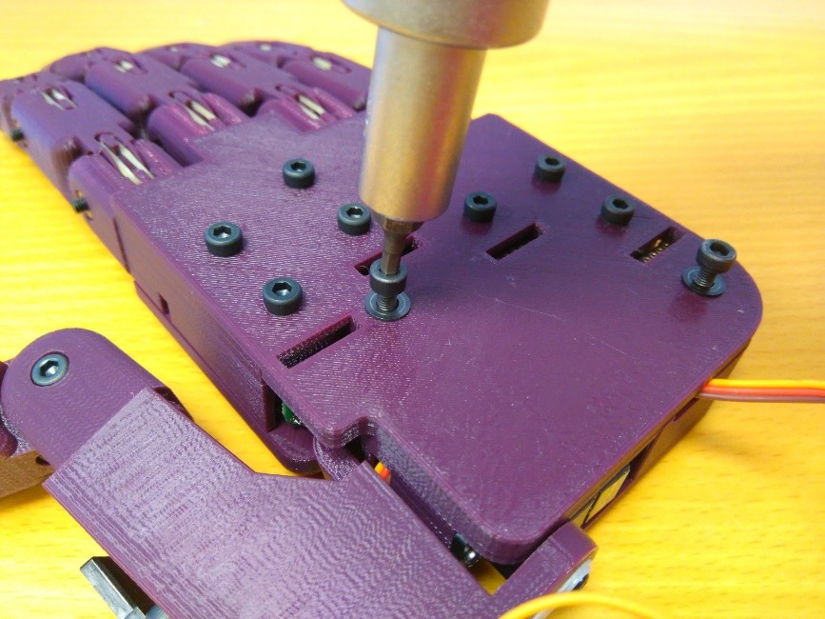
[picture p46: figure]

Finally, put the palm piece covering the actuators and screw two M3x12 bolts to secure the palm in place. Make sure that the cable of the servomotor goes out through the small hole on the lower side of the hand.

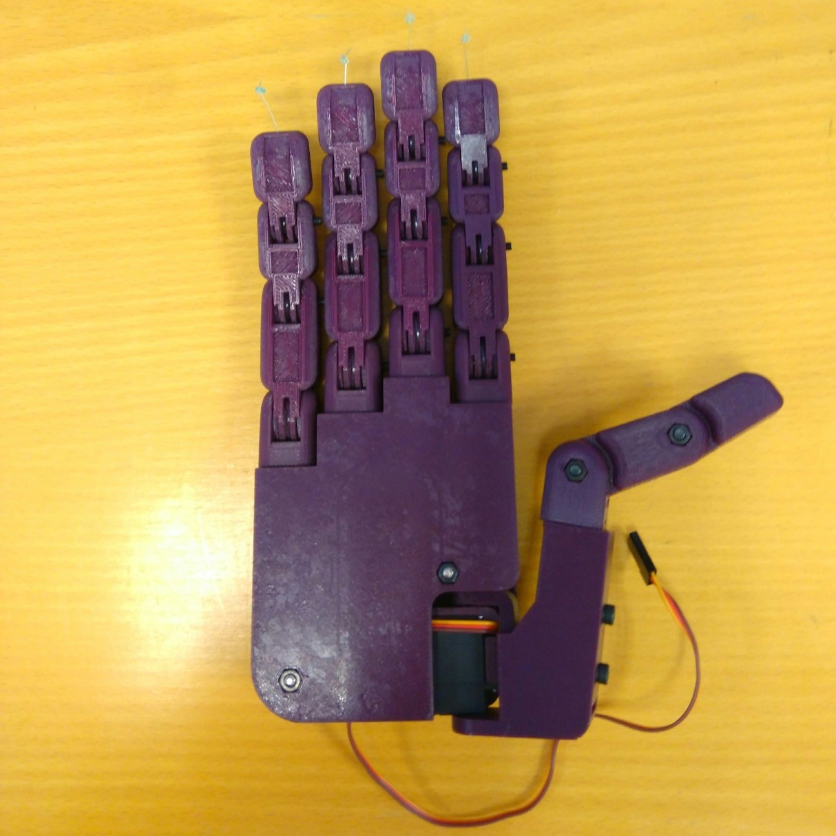
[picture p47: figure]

After following all the previous assembly steps, you will have a fully assembled Dextra hand. Now, you can use it any way you want, as a standalone device or integrated into your own projects. The project is completely open-source, so feel free to modify it and share it. Happy hacking!

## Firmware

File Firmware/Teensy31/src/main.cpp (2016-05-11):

#include <Servo.h>
#include <FlexiTimer2.h>
#include <SeCo.h>

Servo abductor;
SeCo dataLink;

#define pidTime 10 //ms
#define Kp 1000
#define Kd 0
#define winderRadius 4.5
#define angularRes 2*3.14159/6000 //2*pi/number of encoder tics per motor revolution

int abAngle = map(10, 0, 90, 20, 110);

class finger {
private:
    int _encoderPinA, _encoderPinB, _phase, _enable;
    volatile int encoderCount = 0;
    volatile float angularPos = 0, position = 0, setPoint = 0;
    volatile float error = 0, control = 0, lastError = 0, lastPosition = 0;
    int pwmControl = 0;
public:
    void attach(int phase, int enable, int encoderPinA, int encoderPinB, char name) {
        pinMode(encoderPinA, INPUT);
        digitalWrite(encoderPinA, HIGH);
        pinMode(encoderPinB, INPUT);
        digitalWrite(encoderPinA, HIGH);
        pinMode(phase, OUTPUT);
        pinMode(enable, OUTPUT);
        if (name == 't') {
            attachInterrupt(digitalPinToInterrupt(encoderPinA), thumbReadEncoder, CHANGE);
        }
        else if (name == 'i') {
            attachInterrupt(digitalPinToInterrupt(encoderPinA), indexReadEncoder, CHANGE);
        }
        else if (name == 'm') {
            attachInterrupt(digitalPinToInterrupt(encoderPinA), middleReadEncoder, CHANGE);
        }
        else if (name == 'r') {
            attachInterrupt(digitalPinToInterrupt(encoderPinA), ringReadEncoder, CHANGE);
        }
        else if (name == 'p') {
            attachInterrupt(digitalPinToInterrupt(encoderPinA), pinkyReadEncoder, CHANGE);
        }
        _phase = phase;
        _enable = enable;
        _encoderPinA = encoderPinA;
        _encoderPinB = encoderPinB;
    }

    void readEncoder() {
        if (digitalRead(_encoderPinA) == HIGH) {
            if (digitalRead(_encoderPinB) == LOW) {
                encoderCount = encoderCount + 1;
            }
            else {
                encoderCount = encoderCount - 1;
            }
        }
        else {
            if (digitalRead(_encoderPinB) == HIGH) {
                encoderCount = encoderCount + 1;
            }
            else {
                encoderCount = encoderCount - 1;
            }
        }
    }

    void positionPID() {
        angularPos = angularRes*encoderCount;
        position = angularPos*winderRadius;
        error = setPoint - position;
        control = Kp*error + Kd*(error-lastError);
        lastError = error;
        lastPosition = position;
        if ((position > 22)||(position < -12)) {
            analogWrite(_enable, 0);
        }
        else {
            if (control >= 0) {
                pwmControl = constrain(control,0,255);
                digitalWrite(_phase, HIGH);
                if (pwmControl > 25) {
                    analogWrite(_enable, pwmControl);
                }
                else {
                    analogWrite(_enable, 0);
                }
            }
            else {
                pwmControl = constrain(abs(control),0,255);
                digitalWrite(_phase, LOW);
                if (pwmControl > 25) {
                    analogWrite(_enable, pwmControl);
                }
                else {
                    analogWrite(_enable, 0);
                }
            }
        }
    }

    void write(float desiredPosition) {
        cli();
        if (desiredPosition > 22) {
            desiredPosition = 22;
        }
        else if (desiredPosition < -12) {
            desiredPosition = -12;
        }
        setPoint = desiredPosition;
        sei();
    }

    float read(char mode) {
        cli();
        if (mode == 'e') return encoderCount;
        else if (mode == 'a') return angularPos;
        else if (mode == 'p') return position;
        sei();
    }
};

finger thumb;
finger indx;
finger middle;
finger ring;
finger pinky;

void hand_control() {
    thumb.positionPID();
    indx.positionPID();
    middle.positionPID();
    ring.positionPID();
    pinky.positionPID();
}

void thumbReadEncoder() {
    thumb.readEncoder();
}

void indexReadEncoder() {
    indx.readEncoder();
}

void middleReadEncoder() {
    middle.readEncoder();
}

void ringReadEncoder() {
    ring.readEncoder();
}

void pinkyReadEncoder() {
    pinky.readEncoder();
}

void setup() {
    thumb.attach(11,10,15,14,'t');
    indx.attach(8,9,17,16,'i');
    middle.attach(7,6,19,18,'m');
    ring.attach(5,4,21,20,'r');
    pinky.attach(2,3,23,22,'p');
    abductor.attach(12);
    abductor.write(abAngle);
    FlexiTimer2::set(pidTime, hand_control);
    FlexiTimer2::start();
    Serial.begin(115200);
}

void loop() {
    while(!Serial.available());
    char ctrl = Serial.read();
    switch(ctrl) {
        case 't':
            thumb.write(dataLink.receive());
            break;
        case 'i':
            indx.write(dataLink.receive());
            break;
        case 'm':
            middle.write(dataLink.receive());
            break;
        case 'r':
            ring.write(dataLink.receive());
            break;
        case 'p':
            pinky.write(dataLink.receive());
            break;
    }
}

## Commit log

2016-01-07 Hand parts added
    [distal.fcstd, distal_thumb.fcstd, dorsal.fcstd, finger_module.fcstd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]
2016-01-07 .stl added
    [distal.stl, distal_thumb.stl, dorsal.stl, middle.stl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]
2016-01-07 FreeCAD directory added
    [distal.fcstd, distal_thumb.fcstd, dorsal.fcstd, finger_module.fcstd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]
2016-01-08 EMG circuit files added
    [myReaderB.brd, myReaderB.sch]
2016-01-08 Update README.md and project structure
    [distal.fcstd, distal.stl, distal_thumb.fcstd, distal_thumb.stl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]
2016-01-08 Added actuated thumb abduction
    [Turnigy TGY-EX5252.FCStd, abductor.fcstd, dorsal.fcstd, thumb.fcstd]
2016-01-11 Modified abductor and dorsal
    [Turnigy TGY-EX5252.FCStd, abductor.fcstd, abductor.stl, dorsal.fcstd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]
2016-01-12 Added code to control a finger
    [dorsal.stl]
2016-01-21 Added palm and update dorsal
    [dorsal.fcstd, middle.fcstd, palm.fcstd, palm.stl]
2016-01-27 Update parts
    [finger_module.fcstd, motor_holder.fcstd, motor_holder.stl, thumb.fcstd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]
2016-02-17 Update finger_control.ino to control the finger position with a PID
    [abductor.fcstd, jorl.fcstd, palm.fcstd, palm.stl]
2016-02-17 Modified abductor and palm
    [abductor.fcstd, abductor.stl, jorl.fcstd]
2016-02-19 Update finger module to use a Pololu 1000:1 micromotor
    [distal.fcstd, distal.stl, middle.fcstd, middle.stl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]
2016-02-20 Update thumb module and abductor
    [abductor.fcstd, distal_thumb.fcstd, motor_holder_thumb.fcstd]
2016-02-22 Update palm and dorsal
    [dorsal.fcstd, dorsal.stl, palm.fcstd, palm.stl]
2016-02-23 Update finger module
    [distal.fcstd, distal.stl, middle.fcstd, middle.stl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]
2016-02-24 Update thumb module
    [distal_thumb.fcstd, distal_thumb.stl, motor_holder_thumb.fcstd, motor_holder_thumb.stl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]
2016-02-24 Update distal and middle
    [distal.fcstd, distal.stl, middle.fcstd, middle.stl]
2016-02-25 Update abductor
    [abductor.fcstd, abductor.stl]
2016-02-26 Update project structure
    [Turnigy TGY-EX5252.FCStd, abductor.fcstd, abductor.stl, abductor_cover.fcstd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]
2016-02-26 Update assembly
    [abductor_cover.fcstd, motor_holder_thumb.fcstd]
2016-03-02 Update finger_control.ino and send_position.py to control all the fingers
2016-05-11 Added firmware for ST Nucleo board
2016-06-11 Added test code to control the finger force with a PID
2016-07-15 Renamed Teensy firmware to make it compatible with Arduino IDE
2016-07-16 Created library to control fingers
2016-07-26 Added code to receive finger position array
2016-09-06 Added assembly instructions
